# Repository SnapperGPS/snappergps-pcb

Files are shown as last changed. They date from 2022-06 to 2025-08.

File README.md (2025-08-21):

> *Are you looking for the open-source SnapperGPS hardware design files? You can find the files for the original version V1.0.0 in this repository and the files for an updated version V2.0.0 [in another repository](https://github.com/SnapperGPS/snappergps-pcb-2). For differences between both versions, please refer to the documentation over there. Jonas, May 2023*

# snappergps-pcb

The SnapperGPS receiver is a small, low-cost, and low-power GNSS receiver for non-real-time wildlife tracking. It employs the snapshot GNSS technology, which offloads the computationally expensive data processing to the cloud, and:

* Measures 32.0 mm x 27.3 mm,

* Operates for more than a year on a tiny 40 mAh battery,

* Has enough memory to provide almost 11,000 position fixes,

* Captures fixes in user-defined time intervals or externally triggered,

* Needs only 12 ms of signal reception for a fix,

* Employs multiple satellite systems for high reliability (GPS, Galileo, and BeiDou),

* Achieves a median real-world tracking accuracy of about 12 m (before smoothing),

* Maintains a real-time clock to accurately timestamp the fixes,

* Measures the temperature in addition, and

* Is configured via USB in your browser without the need to install a driver or an app.

This repository contains the hardware design files that can be used to replicate a SnapperGPS receiver.

If you use SnapperGPS hardware or software for research, please consider citing our publications.

For the hardware:

> Jonas Beuchert, Amanda Matthes, and Alex Rogers. 2023. SnapperGPS: Open Hardware for Energy-Efficient, Low-Cost Wildlife Location Tracking with Snapshot GNSS. Journal of Open Hardware, 7(1): 2, pp. 1–13. [https://doi.org/10.5334/joh.48](https://openhardware.metajnl.com/articles/10.5334/joh.48/).

For the cloud-processing software:

> Jonas Beuchert and Alex Rogers. 2021. SnapperGPS: Algorithms for Energy-Efficient Low-Cost Location Estimation Using GNSS Signal Snapshots. In SenSys ’21: ACM Conference on Embedded Networked Sensor Systems, November, 2021, Coimbra, Portugal. ACM, New York, NY, USA, 13 pages. https://doi.org/10.1145/3485730.3485931.

**Table of Contents**

1. [Workflow](#workflow)

2. [Getting started](#getting-started)

3. [Repository Structure](#repository-structure)

4. [Professional Manufacturing](#professional-manufacturing)

5. [Hand Assembly](#hand-assembly)

6. [Testing](#testing)

7. [Hardware Overview](#hardware-overview)

8. [Pinout](#pinout)

9. [Bill of Materials](#bill-of-materials)

10. [Additional Resources](#additional-resources)

11. [Acknowledgements](#acknowledgements)

## Workflow

- Get/build your SnapperGPS receiver (see sections below).
- [Configure](https://snappergps.info/configure) your SnapperGPS receiver in your browser for your deployment.
- Deploy your SnapperGPS receiver.
- The SnapperGPS receiver captures GNSS snapshots according to your configuration.
- Recover your SnapperGPS receiver.
- [Upload](https://snappergps.info/upload) the data from your SnapperGPS receiver to our server.
- [Download](https://snappergps.info/view) the track of your surveilled animal.

## Getting started

You already have a SnapperGPS receiver? See [here](GETTING-STARTED.md) how to get started.

You need to build one first? Keep reading.

## Repository Structure

The two files `.brd` and `.sch` are CAD files that contain the PCB's board design and schematic, respectively. They have been created with Autodesk EAGLE 9.6.2, but should be compatible with other electronic design software.

The table `.csv` contains the bill of materials (BOM).

The directory `CAMOutputs` includes the Gerber files and drill file, which are necessary for PCB manufacturing.

The two files `.mnb` and `.mnt` can be used for a pick-and-place machine and describe the component positions and orientations on the bottom and top layer, respectively.

## Professional Manufacturing

The simplest way to replicate SnapperGPS is to upload the BOM, the Gerber files, the drill file, and the pick and place files to an online PCB manufacturing and assembly service. They will source the components, print the PCB, and assemble the board.

We recommend a thickness between 0.8 and 1.6 mm for the two-layered board. The substrate can be FR-4 and hot air solder levelling (HASL) or electroless nickel immersion gold (ENIG) can be used for the finish.

You can find an FAQ on professional manufacturing in [the discussions forum](https://github.com/orgs/SnapperGPS/discussions/22).

## Hand Assembly

An alternative to prefessional manufacturing is to just obtain the SnapperGPS PCB from a PCB manufacturer and to manually assembly the board.
Hand-soldering a board takes less than 2 h for a skilled person, but requires intermediate equipment and skills and potentially additional time for testing, debugging, and re-work.

A laser-cut stencil for applying the solder paste can be helpful and can often be ordered together with the PCB.
In addition, the following materials and equipment are required:

* Soldering paste

* Syringe

* Spatula

* Tweezers

* Hot plate, re-flow oven, or hot air gun

* Flux pen (optional, for re-work)

* Multi-meter (optional, for debugging)

Proceed with the following steps to assemble a SnapperGPS PCB:

* Rigidly fix the PCB to a surface with the top layer pointing up.

* Fix the stencil on the PCB.

* Use the syringe to apply solder paste to the stencil.

* Use the spatula to distribute the solder paste such that all pads on the PCB are covered.

* Remove the stencil.

* Check that all pads are covered with solder paste.

* If not, manually apply solder paste.

* Use tweezers to place the components on the PCB.

* Heat the PCB following the re-flow profile of the used solder paste.

* Test the PCB (see below).

* If it does not work, identify problematic PCB sections and re-work, e.g., by applying flux and re-flowing the board. The most common issues are shorts and missing solder paste on some pads, which can be identified by using a multi-meter for continuity testing, but it is also possible that a component is placed incorrectly.

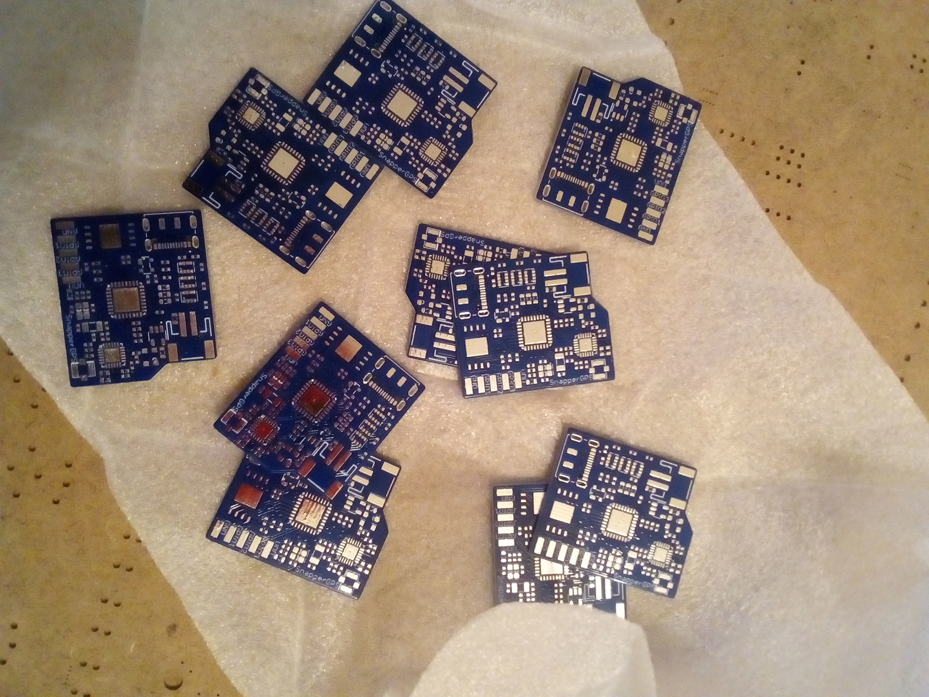
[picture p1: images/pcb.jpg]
SnapperGPS PCB
|  | 
|:--:| 
| *Figure 1: Several SnapperGPS PCBs ready for hand assembly.* |

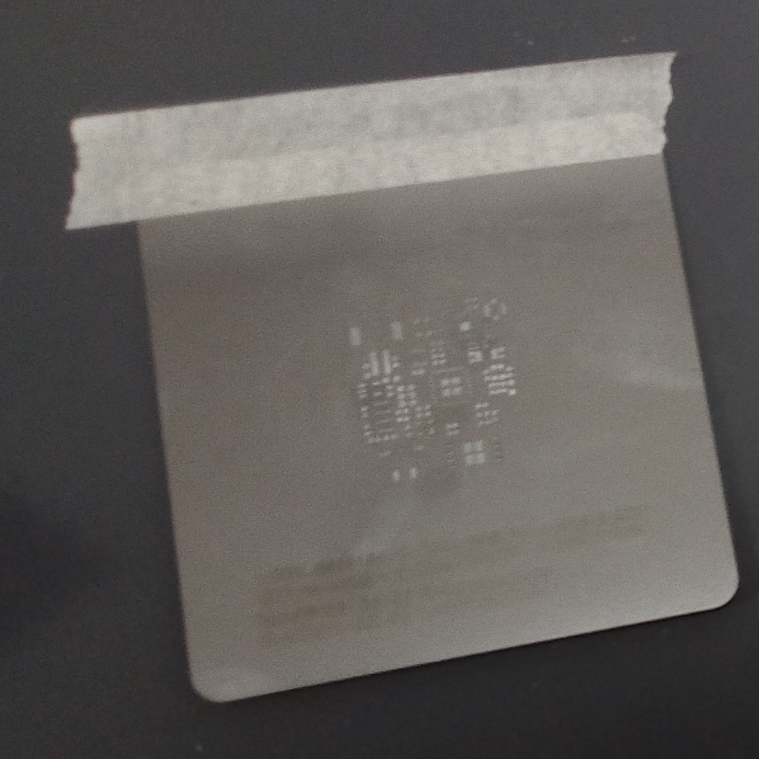
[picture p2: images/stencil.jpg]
Stencil
|  | 
|:--:| 
| *Figure 2: A stencil on top of a SnapperGPS PCB with solder paste applied to it.* |

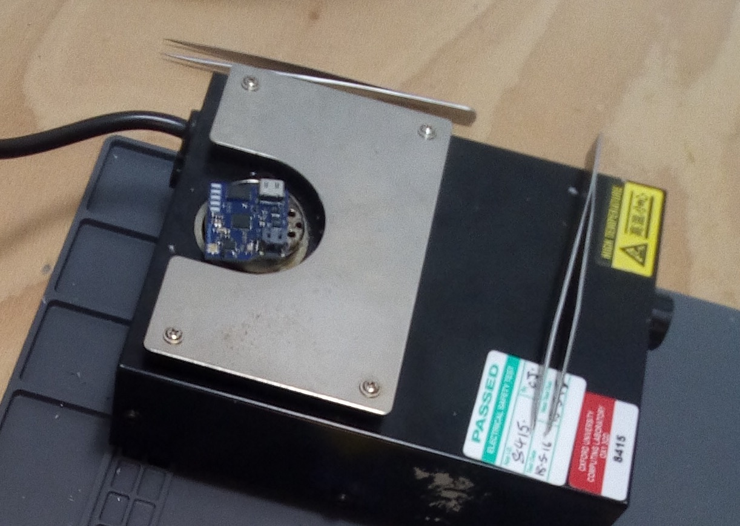
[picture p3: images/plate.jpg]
Hot plate
|  | 
|:--:| 
| *Figure 3: A SnapperGPS PCB with solder paste and components on a hot plate while re-flowing.* |

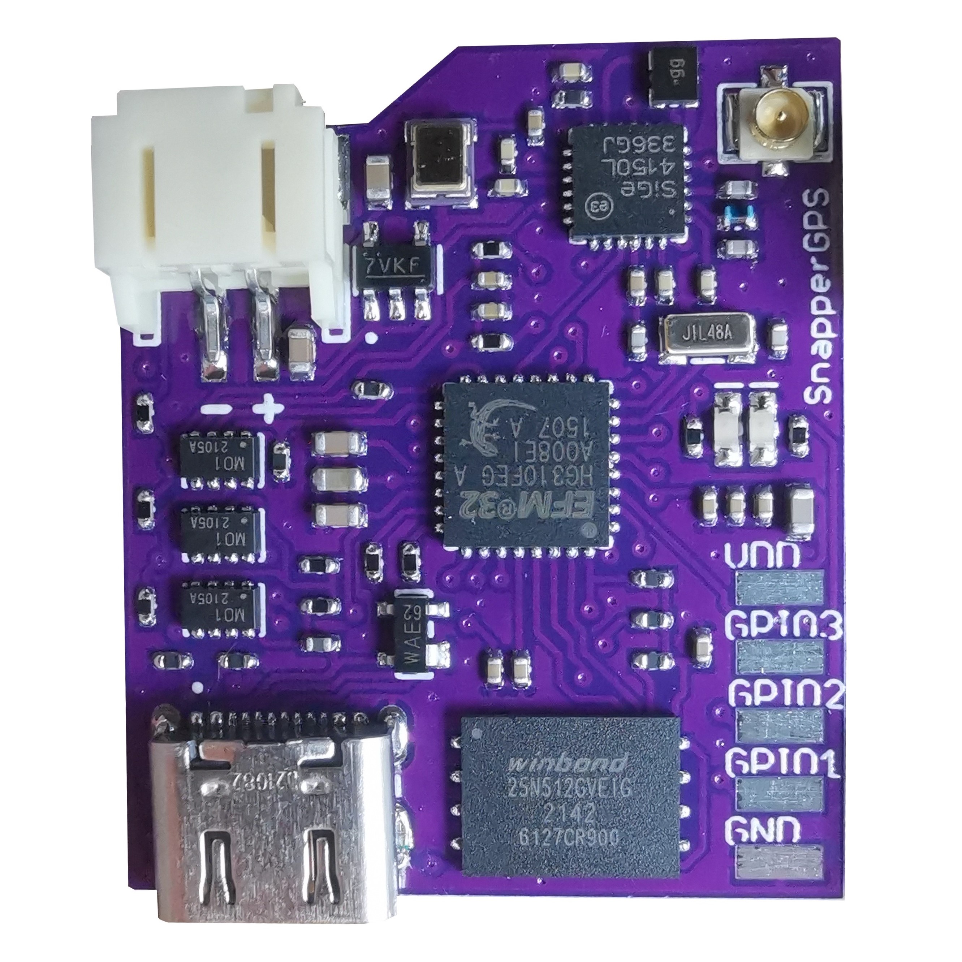
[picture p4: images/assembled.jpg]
Assembled SnapperGPS PCB
|  | 
|:--:| 
| *Figure 4: An assembled SnapperGPS receiver.* |

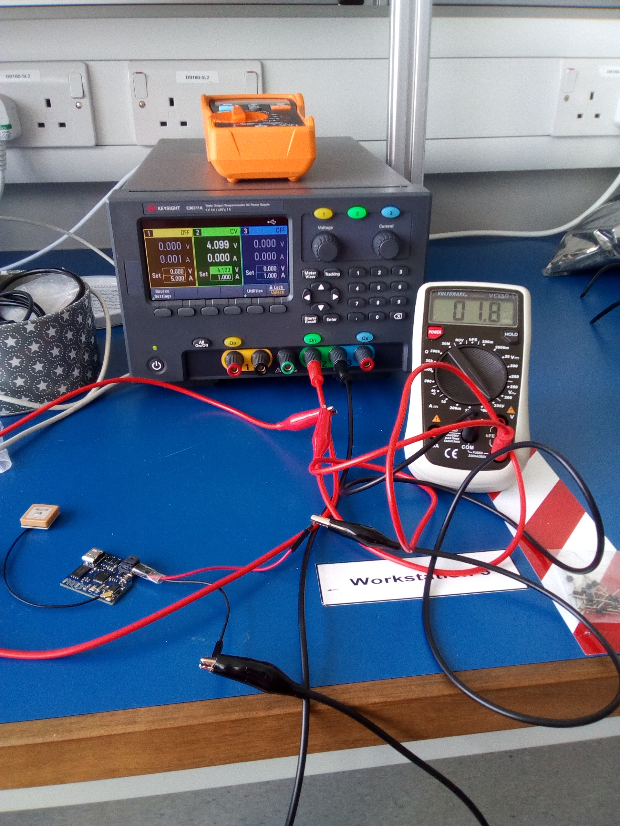
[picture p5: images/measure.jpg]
Measuring the current
|  | 
|:--:| 
| *Figure 5: Measuring the current consumption of an assembled SnapperGPS receiver (bottom left) with a multi-meter (right), a DC voltage source (centre), two jumper wires, and alligator clips.* |

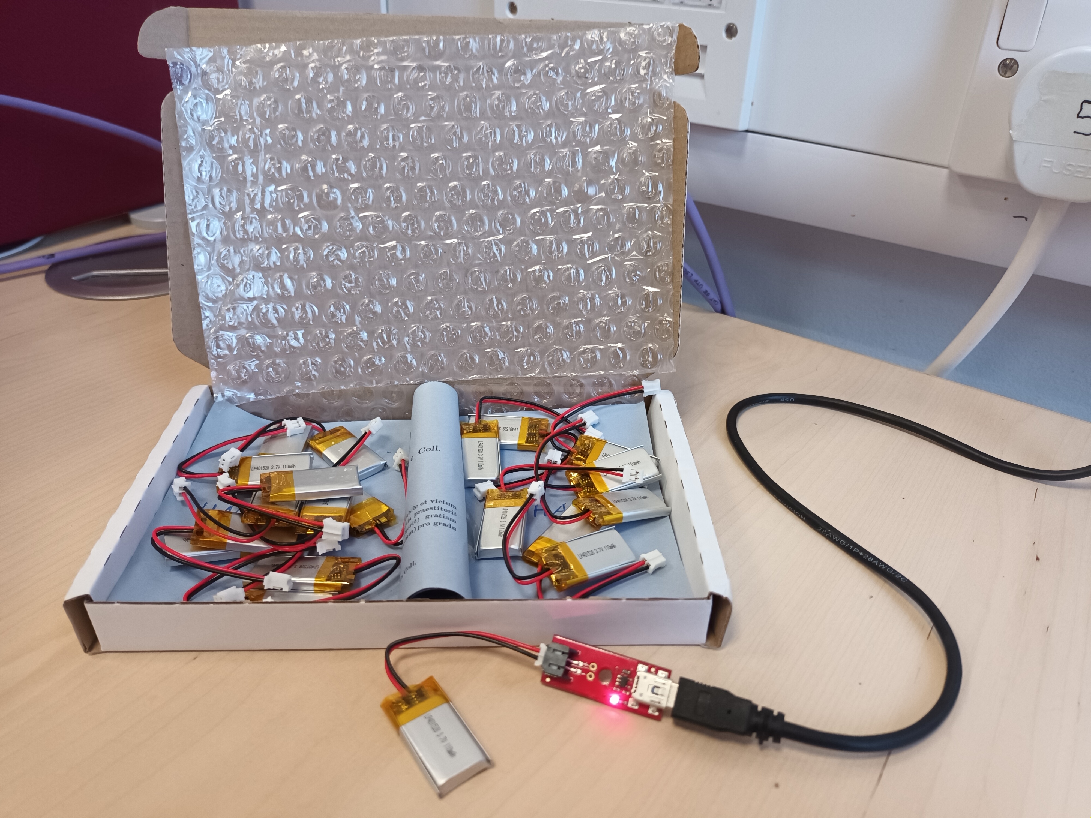
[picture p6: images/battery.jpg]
Charging a battery
|  | 
|:--:| 
| *Figure 6: Charging a 110 mAh lithium-ion polymer battery via USB with a *SparkFun LiPo Charger Basic*.* |

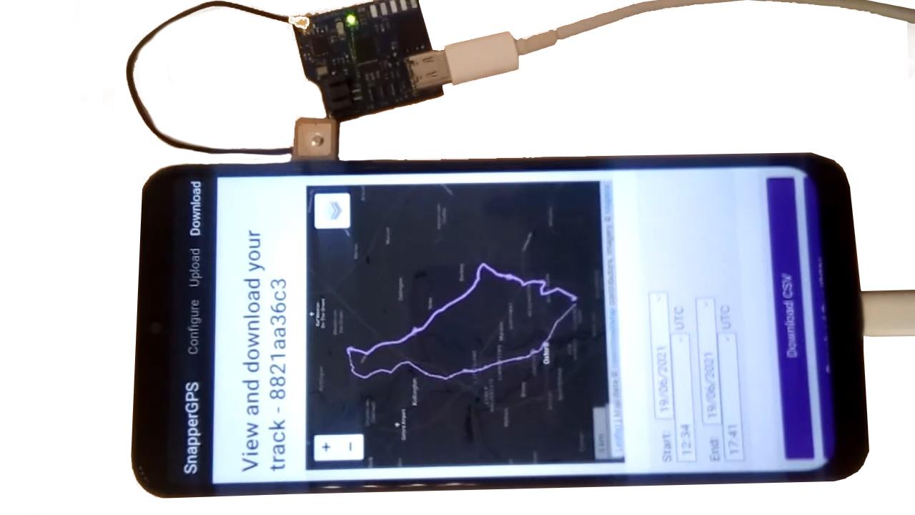
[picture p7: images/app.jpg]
SnapperGPS app
|  | 
|:--:| 
| *Figure 7: Testing a SnapperGPS receiver with the SnapperGPS app on an Android smartphone using a USB-C cable.* |

## Testing

If you replicated a SnapperGPS receiver yourself, you need to flash the SnapperGPS firmware first:

* Short the VDD pin and the SWCLK pin of the SnapperGPS receiver, e.g., with a paper clip.

* Connect the SnapperGPS receiver via a USB-C cable to a host computer.

* Download [the SnapperGPS firmware binary](https://github.com/SnapperGPS/snappergps-firmware/releases).

* Install [the AudioMoth Flash App](https://github.com/OpenAcousticDevices/AudioMoth-Flash-App/releases) **or** [the Silicon Labs Simplicity Commander](https://community.silabs.com/s/article/simplicity-commander).

* Use one of the two tools two flash the firmware binary to the SnapperGPS receiver. (If you use the AudioMoth Flash App, either use v1.4.0 or, if you use v1.6.0, then disable "Clear User Data When Flashing".)

* Remove the paper clip.

Now, you can continue with some basic testing:

* Open [the SnapperGPS web app](https://snappergps.info) in Microsoft Edge or Google Chrome or download it from [the Microsoft Store](https://apps.microsoft.com/store/detail/snappergps/9P9RPRS6LSMM) or [Google Play](https://play.google.com/store/apps/details?id=com.herokuapp.snapper_gps.twa). (Alternatively, you can also host the SnapperGPS web app yourself, as described in [the _snappergps-app_ repository](https://github.com/SnapperGPS/snappergps-app)).

* Go to the *Configure* page and click/tap on *Pair receiver*.

* The connected SnapperGPS receiver should now be selectable in a pop-up window.

* After pairing, confirm that the receiver information in the table on the top of the page is appropriate, including on-board time and firmware version. The snapshot count should be zero.

* Connect a LiPo battery to the SnapperGPS receiver, paying attention to the polarity markers on top of the PCB. Connect the black cable to the pin next to the *-* and the red cable to the pin next to the *+*.

* Check the measured battery voltage in the table at the top of the *Configure* page. We recommend charging the battery to at least 4.1 V before a long-term deployment.

* Connnect an active GNSS antenna of your choice via the U.FL connector to the SnapperGPS receiver.

* Select some configuration parameters in the app and click/tap on *Configure*.

* Disconnect the SnapperGPS receiver.

* Record a few snapshots outdoors.

* Reconnect the SnapperGPS receiver.

* Go to the *Upload* page and follow the instructions to upload the snapshots from the SnapperGPS receiver to the server. Please select only snapshots for processing that you collected outdoors.

* Once processing is complete, inspect the calculated track on the *Download* page. There are also links to some of our tracks for comparison.

Testing the localisation accuracy:

* Record some data outdoors at a location with known coordinates.

* Upload it via the SnapperGPS app.

* Calculate the horizontal error between the estimated locations and the ground truth.

* We obtained median errors of 10-12 m, depending on the scenario.

Measuring the power consumption:

* Configure a SnapperGPS receiver using the SnapperGPS app.

* Power the SnapperGPS receiver from an external DC source with 3.7-4.2 V.

* Place an ammeter in series with the source.

* The current should be 1-2 μA if the board is sleeping and the maximum current should be around 25 mA when capturing a snapshot. The charge consumption for a single snapshot should be <0.3 μAh.

Testing the flash memory:

* Record the maximum of 10901 snapshots.

* Transfer them to a host computer using the *Transfer data* button on the *Upload* page of the SnapperGPS web app.

* Ensure that all 10901 snapshots have been transferred and are provided as download.

## Hardware Overview

Please have a look at our [paper](https://doi.org/10.5334/joh.48).

## Pinout

We expose the three general-purpose input/output pins (GPIOs) PA0, PA1, and PA2 of the MCU as well as the supply voltage pin VDD and the ground pin GND at an edge of the PCB.
This allows to connect external modules to extend the functionality of the device.
This can be done by soldering wires on the rectangular pads.
For the functionality of the three pins, please refer to [the pinout section in the datasheet of the EFM32HG310](https://www.silabs.com/documents/public/data-sheets/efm32hg-datasheet.pdf#page=118).

We also expose the VDD, GND, RESET, SWCLK, and SWDIO pins of the MCU on the back of the PCB.
The last two ones allow for debugging or flashing using [Serial Wire Debug (SWD)](https://community.silabs.com/s/article/serial-wire-debug-swd-x).
All five circular pads have a spacing of 0.1 in and, hence, the same as common PCB headers.

All ten pads are labelled on the silkscreen of the PCB.

```
Front           │           │ Back
                │           │
                │           │ ○ GND
          VDD □ │           │
                │           │ ○ RESET
    GPIO3/PA2 □ │           │
                │           │ ○ SWCLK
    GPIO2/PA1 □ │           │
                │           │ ○ SWDIO
    GPIO1/PA0 □ │           │
                │           │ ○ VDD
          GND □ │           │
────────────────┘           │
```

## Bill of Materials

|Designator                                    |Qty|Manufacturer                  |Part #                                 |Description/Value                                            |Package/Footprint|Mounting Type|Notes                                                                          |Supplier URL                                                                                           |
|----------------------------------------------|--:|------------------------------|---------------------------------------|-------------------------------------------------------------|-----------------|-------------|-------------------------------------------------------------------------------|-------------------------------------------------------------------------------------------------------|
|C4, C8, C10, C12, C13, C14, C16, C17, C20, C23| 10|Murata                        |GRM155R60J104KA01D                     |Ceramic capacitor, 100 nF                                    |0402             |SMD          |                                                                               |https://www.digikey.com/en/products/detail/murata-electronics/GRM155R60J104KA01D/490-6287-1-ND/3845484 |
|C3, C5, C6, C7, C9                            |  5|Murata                        |GRM155R60J103KA01D                     |Ceramic capacitor, 10 nF                                     |0402             |SMD          |                                                                               |https://www.digikey.com/en/products/detail/murata-electronics/GRM155R60J103KA01D/490-6286-1-ND/3845483 |
|C2                                            |  1|Murata                        |GRM1555C1H101JA01J                     |Ceramic capacitor, 100 pF                                    |0402             |SMD          |                                                                               |https://www.digikey.com/en/products/detail/murata-electronics/GRM1555C1H101JA01J/490-7754-1-ND/4358006 |
|C1                                            |  1|Murata                        |GRM1555C1H220JA01D                     |Ceramic capacitor, 22 pF                                     |0402             |SMD          |                                                                               |https://www.digikey.com/en/products/detail/murata-electronics/GRM1555C1H220JA01D/490-5868-1-ND/3175200 |
|C21, C22                                      |  2|Murata                        |GRM1555C1H180JA01D                     |Ceramic capacitor, 18 pF                                     |0402             |SMD          |                                                                               |https://www.digikey.com/en/products/detail/murata-electronics/GRM1555C1H180JA01D/2854383               |
|C11, C19, C24, C25                            |  4|Murata                        |GRM188R60J105KA01D                     |Multi-layer ceramic capacitor, 1 uF, 6.3 V, X5R              |0603             |SMD          |                                                                               |https://www.digikey.com/en/products/detail/murata-electronics/GRM188R60J105KA01D/490-1550-1-ND/587755  |
|C18                                           |  1|Murata                        |GRM185R60J475ME15D                     |Multi-layer ceramic capacitor, 4.7 uF, 6.3 V, X5R            |0603             |SMD          |                                                                               |https://www.digikey.com/en/products/detail/murata-electronics/GRM185R60J475ME15D/490-3892-1-ND/965934  |
|C15                                           |  1|Murata                        |GRM188R60J106KE47D                     |Multi-layer ceramic capacitor, 10 uF, 6.3 V, X5R             |0603             |SMD          |                                                                               |https://www.digikey.com/en/products/detail/murata-electronics/GRM188R60J106KE47D/490-12538-1-ND/5797528|
|L1                                            |  1|Delta Electronics             |0402HS-390EKTS                        |Fixed inductor, 39 nH, 200 mA, 550 MOhm                      |0402             |SMD          |                                                                               |https://www.digikey.com/en/products/detail/0402HS-390EKTS/2035-0402HS-390EKTSCT-ND/10231211            |
|L2                                            |  1|Murata                        |BLM15HB221SH1D                         |Ferrite bead                                                 |0402             |SMD          |                                                                               |https://www.digikey.com/en/products/detail/murata-electronics/BLM15HB221SH1D/6798444                   |
|R11, R12                                      |  2|Yageo                         |RC0402FR-0715RL                        |Resistor, 15R                                                |0402             |SMD          |                                                                               |https://www.digikey.com/en/products/detail/yageo/RC0402FR-0715RL/311-15LRCT-ND/2827914                 |
|R15, R16                                      |  2|Yageo                         |RC0402FR-071KL                         |Resistor, 1K                                                 |0402             |SMD          |                                                                               |https://www.digikey.com/en/products/detail/yageo/RC0402FR-071KL/726513                                 |
|R10, R13, R17                                 |  3|Yageo                         |RC0402FR-074K7L                        |Resistor, 4K7                                                |0402             |SMD          |                                                                               |https://www.digikey.com/en/products/detail/yageo/RC0402FR-074K7L/311-4-7KLRCT-ND/2827881               |
|R7, R8                                        |  2|Yageo                         |RC0402FR-075K1L                        |Resistor, 5K1                                                |0402             |SMD          |                                                                               |https://www.digikey.com/en/products/detail/yageo/RC0402FR-075K1L/726624                                |
|R18                                           |  1|Yageo                         |RC0402FR-076K8L                        |Resistor, 6K8                                                |0402             |SMD          |                                                                               |https://www.digikey.com/en/products/detail/yageo/RC0402FR-076K8L/311-6-80KLRCT-ND/729589               |
|R14, R19                                      |  2|Yageo                         |RC0402FR-0710KL                        |Resistor, 10K                                                |0402             |SMD          |                                                                               |https://www.digikey.com/en/products/detail/yageo/RC0402FR-0710KL/726523                                |
|R1, R2, R3, R4, R5, R6, R9                    |  7|Yageo                         |RC0402FR-07100KL                       |Resistor, 100K                                               |0402             |SMD          |                                                                               |https://www.digikey.com/en/products/detail/yageo/RC0402FR-07100KL/311-100KLRCT-ND/729473               |
|Q2                                            |  1|Jauch Quartz                  |Q 0,032768-JTX310-12,5-10-T1-HMR-50K-LF|Crystal, 32.768 kHz ±10 ppm, 12.5 pF, 50 kOhm                |2-SMD            |SMD          |Possible substitutes: Epsom, X1A0001410004 FC-135R 32.768KHZ 9PF or Jauch Quartz, Q 0,032768-JTX310-12,5-10-T1-HMR-60K-LF|https://www.digikey.com/en/products/detail/jauch-quartz/Q-0-032768-JTX310-12-5-10-T1-HMR-50K-LF/8108077|
|D1                                            |  1|Rohm Semiconductor            |SML-D12M1WT86                          |LED, yellow-green, 572 nm, 2.2 V                             |0603             |SMD          |                                                                               |https://www.digikey.com/en/products/detail/rohm-semiconductor/SML-D12M1WT86/SML-D12M1WT86CT-ND/5843861 |
|D2                                            |  1|Rohm Semiconductor            |SML-D12U1WT86                          |LED, red, 620 nm, 2.2 V                                      |0603             |SMD          |                                                                               |https://www.digikey.com/en/products/detail/rohm-semiconductor/SML-D12U1WT86/SML-D12U1WT86CT-ND/5843858 |
|TCXO1                                         |  1|Connor Winfield               |D32G-016.368M                          |Temperature compensated oscillator, 16.384 MHz               |3.2x2.5          |SMD          |Possible substitutes: EPSON, X1G005441030112 or TXC Corporation, 7Q-16.368MBG-T|https://www.digikey.com/en/products/detail/connor-winfield/D32G-016-368M/3641696                       |
|U2                                            |  1|Skyworks Solutions Inc.       |SE4150L-R                              |RF receiver                                                  |24-QFN           |SMD          |                                                                               |https://www.digikey.com/en/products/detail/skyworks-solutions-inc/SE4150L-R/863-1354-1-ND/2745473      |
|SAW1                                          |  1|Abracon LLC                   |AFS20A42-1575.42-T3                    |SAW filter, 1.575 GHz, BW 42 MHz                             |4-SMD            |SMD          |Possible substitute: AFS20A02-1575.42-T3                                       |https://www.digikey.com/en/products/detail/abracon-llc/AFS20A42-1575-42-T3/535-12069-1-ND/4075659      |
|U1                                            |  1|Silicon Labs                  |EFM32HG310F64G-C-QFN32R                |Microcontroller                                              |32-QFN           |SMD          |Possible substitutes: EFM32HG310F64G-A-QFN32R or EFM32HG310F64G-B-QFN32R       |https://www.digikey.com/en/products/detail/silicon-labs/EFM32HG310F64G-C-QFN32R/336-6165-1-ND/10314104 |
|U3                                            |  1|Nexperia                      |PRTR5V0U2AX,235                        |TVS diode, 5.5 V                                             |SOT143B          |SMD          |                                                                               |https://www.digikey.com/en/products/detail/nexperia-usa-inc/PRTR5V0U2AX235/1727-5862-1-ND/2698064      |
|IC1                                           |  1|Winbond Electronics           |W25N512GVEIG                           |NAND flash, 512 Mbit                                         |WSON-8           |SMD          |                                                                               |https://www.digikey.com/en/products/detail/W25N512GVEIG/256-W25N512GVEIG-ND/12143334                   |
|J3                                            |  1|TE Connectivity AMP Connectors|1909763-1                              |U.FL connector jack, 50 Ohm                                  |                 |SMD          |                                                                               |https://www.digikey.com/en/products/detail/1909763-1/A118077CT-ND/4729711                              |
|Q1, Q3, Q4                                    |  3|Rohm Semiconductor            |TT8M1TR                                |Mosfet array N and P-channel, 20 V, 2.5 A, 1 W               |8-SMD            |SMD          |                                                                               |https://www.digikey.com/en/products/detail/rohm-semiconductor/TT8M1TR/5042837                          |
|U4                                            |  1|ABLIC U.S.A. Inc.             |S-1318D33-M5T1U4                       |Linear voltage regulator IC, positive fixed, 1 output, 100 mA|SOT-23-5         |SMD          |                                                                               |https://www.digikey.com/en/products/detail/ablic-inc/S-1318D33-M5T1U4/10313979                         |
|J1                                            |  1|JAE Electronics               |DX07S016JA1R1500                       |USB-C receptacle connector, 24 Pins (16+8 dummy), right angle|                 |through-hole |                                                                               |https://www.digikey.com/en/products/detail/jae-electronics/DX07S016JA1R1500/11585731                   |
|J2                                            |  1|JST Sales America Inc.        |S2B-PH-SM4-TB                          |Connector header, right angle, 2 position, 2.00 mm           |                 |SMD          |                                                                               |https://www.digikey.com/en/products/detail/jst-sales-america-inc/S2B-PH-SM4-TB-LF-SN/926655            |
|                                              |   |                              |                                       |                                                             |                 |             |                                                                               |                                                                                                       |

The BOM differs slightly from the one for initial SnapperGPS test boards, which was only $14 in a batch of 100.
For example, we used cheaper TCXOs, the X1G005441030112 manufactured by EPSON or the 7Q-16.368MBG-T from the TXC Corporation, which cost around $2 instead of the expensive D32G-016.368M that costs $7-$8.
We had to introduce this change because of the on-going global supply chain disruptions and recommend to revert to one of the initial choices for replications, if possible, to reduce the overall cost.

## Additional resources

## Acknowledgements

SnapperGPS is developed by
[Jonas Beuchert](https://users.ox.ac.uk/~kell5462/),
[Amanda Matthes](https://amanda-matthes.github.io/), and
[Alex Rogers](https://www.cs.ox.ac.uk/people/alex.rogers/)
in the Department of Computer Science
of the University of Oxford.

Jonas Beuchert and Amanda Matthes are
funded by the EPSRC Centre for Doctoral Training in
Autonomous Intelligent Machines and Systems
(DFT00350-DF03.01, DFT00350-DF03.05) and develop
SnapperGPS as part of their doctoral studies.
The implementation of SnapperGPS 
was co-funded by an EPSRC IAA Technology Fund
(D4D00010-BL14).

[Amanda Matthes](https://github.com/amanda-matthes) owns the copyright of the current SnapperGPS logo/icon that is on the bottom layer silkscreen of the PCB.

##

This documentation is licensed under a
[Creative Commons Attribution 4.0 International License][cc-by].

[][cc-by]

[cc-by]: http://creativecommons.org/licenses/by/4.0/
[cc-by-image]: https://i.creativecommons.org/l/by/4.0/88x31.png

SnapperGPS V1.0.0 is certified as open source hardware by the Open Source Hardware Association with UID [UK000044](https://certification.oshwa.org/uk000044.html).

OSHWA certification

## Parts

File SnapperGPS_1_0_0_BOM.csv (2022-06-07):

Designator | Qty | Manufacturer | Part # | Description/Value | Package/Footprint | Mounting Type | Notes | Supplier URL | Price (1 set) [USD] | Price (100 sets) [USD] | Price (1000 sets) [USD]
C4, C8, C10, C12, C13, C14, C16, C17, C20, C23 | 10 | Murata | GRM155R60J104KA01D | Ceramic capacitor, 100 nF | 402 | SMD |  | https://www.digikey.com/en/products/detail/murata-electronics/GRM155R60J104KA01D/490-6287-1-ND/3845484 | 0.33 | 14.6 | 81.7
C3, C5, C6, C7, C9 | 5 | Murata | GRM155R60J103KA01D | Ceramic capacitor, 10 nF | 402 | SMD |  | https://www.digikey.com/en/products/detail/murata-electronics/GRM155R60J103KA01D/490-6286-1-ND/3845483 | 0.5 | 4.43 | 29.1
C2 | 1 | Murata | GRM1555C1H101JA01J | Ceramic capacitor, 100 pF | 402 | SMD |  | https://www.digikey.com/en/products/detail/murata-electronics/GRM1555C1H101JA01J/490-7754-1-ND/4358006 | 0.1 | 0.81 | 4.54
C1 | 1 | Murata | GRM1555C1H220JA01D | Ceramic capacitor, 22 pF | 402 | SMD |  | https://www.digikey.com/en/products/detail/murata-electronics/GRM1555C1H220JA01D/490-5868-1-ND/3175200 | 0.1 | 0.81 | 4.57
C21, C22 | 2 | Murata | GRM1555C1H180JA01D | Ceramic capacitor, 18 pF | 402 | SMD |  | https://www.digikey.com/en/products/detail/murata-electronics/GRM1555C1H180JA01D/2854383 | 0.2 | 2.32 | 13
C11, C19, C24, C25 | 4 | Murata | GRM188R60J105KA01D | Multi-layer ceramic capacitor, 1 uF, 6.3 V, X5R | 603 | SMD |  | https://www.digikey.com/en/products/detail/murata-electronics/GRM188R60J105KA01D/490-1550-1-ND/587755 | 0.4 | 11 | 61.84
C18 | 1 | Murata | GRM185R60J475ME15D | Multi-layer ceramic capacitor, 4.7 uF, 6.3 V, X5R | 603 | SMD |  | https://www.digikey.com/en/products/detail/murata-electronics/GRM185R60J475ME15D/490-3892-1-ND/965934 | 0.3 | 11.67 | 72.02
C15 | 1 | Murata | GRM188R60J106KE47D | Multi-layer ceramic capacitor, 10 uF, 6.3 V, X5R | 603 | SMD |  | https://www.digikey.com/en/products/detail/murata-electronics/GRM188R60J106KE47D/490-12538-1-ND/5797528 | 0.15 | 5.07 | 29.44
L1 | 1 | Delta Electronics | 0402HS-390EKTS | Fixed inductor, 39 nH, 200 mA, 550 MOhm | 402 | SMD |  | https://www.digikey.com/en/products/detail/0402HS-390EKTS/2035-0402HS-390EKTSCT-ND/10231211 | 0.26 | 15.68 | 109.72
L2 | 1 | Murata | BLM15HB221SH1D | Ferrite bead | 402 | SMD |  | https://www.digikey.com/en/products/detail/murata-electronics/BLM15HB221SH1D/6798444 | 0.1 | 4.36 | 25.08
R11, R12 | 2 | Yageo | RC0402FR-0715RL | Resistor, 15R | 402 | SMD |  | https://www.digikey.com/en/products/detail/yageo/RC0402FR-0715RL/311-15LRCT-ND/2827914 | 0.2 | 1.32 | 5.98
R15, R16 | 2 | Yageo | RC0402FR-071KL | Resistor, 1K | 402 | SMD |  | https://www.digikey.com/en/products/detail/yageo/RC0402FR-071KL/726513 | 0.2 | 1.32 | 5.98
R10, R13, R17 | 3 | Yageo | RC0402FR-074K7L | Resistor, 4K7 | 402 | SMD |  | https://www.digikey.com/en/products/detail/yageo/RC0402FR-074K7L/311-4-7KLRCT-ND/2827881 | 0.3 | 1.98 | 7.77
R7, R8 | 2 | Yageo | RC0402FR-075K1L | Resistor, 5K1 | 402 | SMD |  | https://www.digikey.com/en/products/detail/yageo/RC0402FR-075K1L/726624 | 0.2 | 1.32 | 5.98
R18 | 1 | Yageo | RC0402FR-076K8L | Resistor, 6K8 | 402 | SMD |  | https://www.digikey.com/en/products/detail/yageo/RC0402FR-076K8L/311-6-80KLRCT-ND/729589 | 0.1 | 0.66 | 2.99
R14, R19 | 2 | Yageo | RC0402FR-0710KL | Resistor, 10K | 402 | SMD |  | https://www.digikey.com/en/products/detail/yageo/RC0402FR-0710KL/726523 | 0.2 | 1.32 | 5.98
R1, R2, R3, R4, R5, R6, R9 | 7 | Yageo | RC0402FR-07100KL | Resistor, 100K | 402 | SMD |  | https://www.digikey.com/en/products/detail/yageo/RC0402FR-07100KL/311-100KLRCT-ND/729473 | 0.7 | 4.62 | 14.98
Q2 | 1 | Jauch Quartz | Q 0,032768-JTX310-12,5-10-T1-HMR-50K-LF | Ctystal, 32.768 kHz ±10 ppm, 12.5 pF, 50 kOhm | 2-SMD | SMD | Possible substitute: Epsom, X1A0001410004 FC-135R 32.768KHZ 9PF | https://www.digikey.com/en/products/detail/jauch-quartz/Q-0-032768-JTX310-12-5-10-T1-HMR-50K-LF/8108077 | 0.86 | 62.7 | 495
D1 | 1 | Rohm Semiconductor | SML-D12M1WT86 | LED, yellow-green, 572 nm, 2.2 V | 603 | SMD |  | https://www.digikey.com/en/products/detail/rohm-semiconductor/SML-D12M1WT86/SML-D12M1WT86CT-ND/5843861 | 0.22 | 5.51 | 39.86
D2 | 1 | Rohm Semiconductor | SML-D12U1WT86 | LED, red, 620 nm, 2.2 V | 603 | SMD |  | https://www.digikey.com/en/products/detail/rohm-semiconductor/SML-D12U1WT86/SML-D12U1WT86CT-ND/5843858 | 0.22 | 5.51 | 39.86
TCXO1 | 1 | Connor Winfield | D32G-016.368M | Temperature compensated oscillator, 16.384 MHz | 3.2x2.5 | SMD | Possible substitutes: EPSON, X1G005441030112 or TXC Corporation, 7Q-16.368MBG-T | https://www.digikey.com/en/products/detail/connor-winfield/D32G-016-368M/3641696 | 8 | 700 | 7000
U2 | 1 | Skyworks Solutions Inc. | SE4150L-R | RF receiver | 24-QFN | SMD |  | https://www.digikey.com/en/products/detail/skyworks-solutions-inc/SE4150L-R/863-1354-1-ND/2745473 | 0.86 | 86.4 | 864
SAW1 | 1 | Abracon LLC | AFS20A42-1575.42-T3 | SAW filter, 1.575 GHz, BW 42 MHz | 4-SMD | SMD |  | https://www.digikey.com/en/products/detail/abracon-llc/AFS20A42-1575-42-T3/535-12069-1-ND/4075659 | 1.05 | 71.37 | 543.74
U1 | 1 | Silicon Labs | EFM32HG310F64G-C-QFN32R | Microcontroller | 32-QFN | SMD |  | https://www.digikey.com/en/products/detail/silicon-labs/EFM32HG310F64G-C-QFN32R/336-6165-1-ND/10314104 | 5.91 | 435.04 | 3703.46
U3 | 1 | Nexperia | PRTR5V0U2AX,235 | TVS diode, 5.5 V | SOT143B | SMD |  | https://www.digikey.com/en/products/detail/nexperia-usa-inc/PRTR5V0U2AX235/1727-5862-1-ND/2698064 | 0.66 | 42.47 | 257.87
IC1 | 1 | Winbond Electronics | W25N512GVEIG | NAND flash, 512 Mbit | WSON-8 | SMD |  | https://www.digikey.com/en/products/detail/W25N512GVEIG/256-W25N512GVEIG-ND/12143334 | 2.9 | 228.68 | 2051.92
J3 | 1 | TE Connectivity AMP Connectors | 1909763-1 | U.FL connector jack, 50 Ohm |  | SMD |  | https://www.digikey.com/en/products/detail/1909763-1/A118077CT-ND/4729711 | 0.51 | 36.55 | 595.9
Q1, Q3, Q4 | 3 | Rohm Semiconductor | TT8M1TR | Mosfet array N and P-channel, 20 V, 2.5 A, 1 W | 8-SMD | SMD |  | https://www.digikey.com/en/products/detail/rohm-semiconductor/TT8M1TR/5042837 | 1.56 | 86.58 | 487.08
U4 | 1 | ABLIC U.S.A. Inc. | S-1318D33-M5T1U4 | Linear voltage regulator IC, positive fixed, 1 output, 100 mA | SOT-23-5 | SMD |  | https://www.digikey.com/en/products/detail/ablic-inc/S-1318D33-M5T1U4/10313979 | 1.58 | 109.94 | 908.2
J1 | 1 | JAE Electronics | DX07S016JA1R1500 | USB-C receptacle connector, 24 Pins (16+8 dummy), right angle |  | through-hole |  | https://www.digikey.com/en/products/detail/jae-electronics/DX07S016JA1R1500/11585731 | 1.67 | 129.65 | 1080.44
J2 | 1 | JST Sales America Inc. | S2B-PH-SM4-TB | Connector header, right angle, 2 position, 2.00 mm |  | SMD |  | https://www.digikey.com/en/products/detail/jst-sales-america-inc/S2B-PH-SM4-TB-LF-SN/926655 | 0.54 | 39.08 | 339.84
 |  |  |  |  |  |  |  |  | 31.55 | 2124.54 | 18900.69

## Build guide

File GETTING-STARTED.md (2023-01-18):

# SnapperGPS: Getting started

You just obtained your first SnapperGPS receiver or built one yourself? Here is how to get started with a quick test. If you face any problems on the way, check our troubleshooting section on [https://snappergps.info/](https://snappergps.info/), ask a question [on GitHub](https://github.com/orgs/SnapperGPS/discussions), or create [a new troubleshooting issue](https://github.com/SnapperGPS/snappergps-pcb/issues).

## What is in the box?

SnapperGPS receivers come as assembled PCBs, but without any further protection or peripherals.

| A bare-bone SnapperGPS receiver |
|:--:|
| *Figure 1: A bare-bone SnapperGPS receiver.* |

## What you need in addition.

To make your SnapperGPS receiver fully functional, you need the following items:
-	An active GPS-L1 antenna with [a U.FL/IPEX connector](https://en.wikipedia.org/wiki/Hirose_U.FL), for example, [an Echo 27](https://www.siretta.com/products/antennas/echo-27/), [an Abracon APAM1368YB13V3.0](https://abracon.com/parametric/antennas/APAM1368YB13V3.0), or [an Abracon APAM2764YK0175](https://abracon.com/parametric/antennas/APAM2764YK0175). More information [here](https://github.com/SnapperGPS/snappergps-pcb/discussions/10).
-	A lithium-ion polymer (LiPo) battery with a JST-PH connector to power your SnapperGPS receiver during a deployment, for example [this one with 40 mAh](https://www.sparkfun.com/products/13852) or [this one with 110 mAh](https://www.sparkfun.com/products/13853). Make sure that the polarity is correct, i.e., the same as in Figure 2 and **not** as in Figure 3.
-	Optionally, a charger for your LiPo battery. More information [here](https://github.com/SnapperGPS/snappergps-pcb/discussions/6).
-	A USB-C cable to connect your SnapperGPS receiver to your laptop, desktop computer, phone, or tablet. This must be a power+data cable, not a power-only cable.

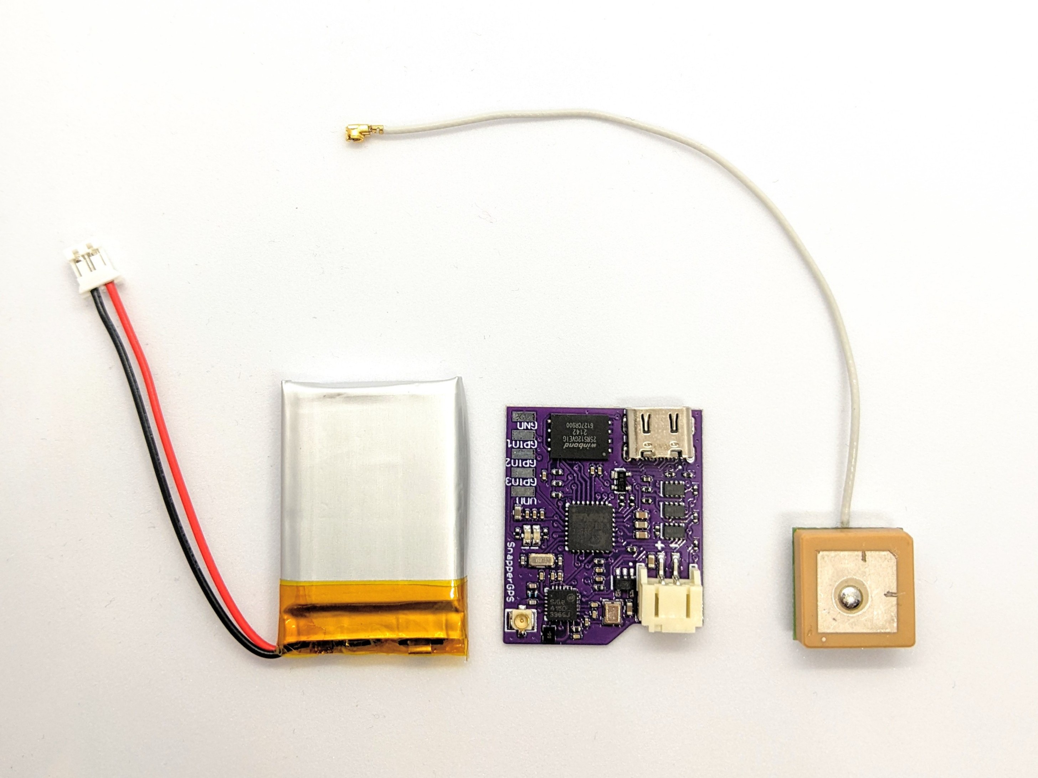
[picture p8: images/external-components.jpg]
A SnapperGPS receiver, an Echo 27 antenna (right), and a 400 mAh lithium-polymer battery (left)
|  |
|:--:|
| *Figure 2: A SnapperGPS receiver, an Echo 27 antenna (right), and a lithium-ion polymer battery with a JST-PH connector with the correct polarity (left).* |

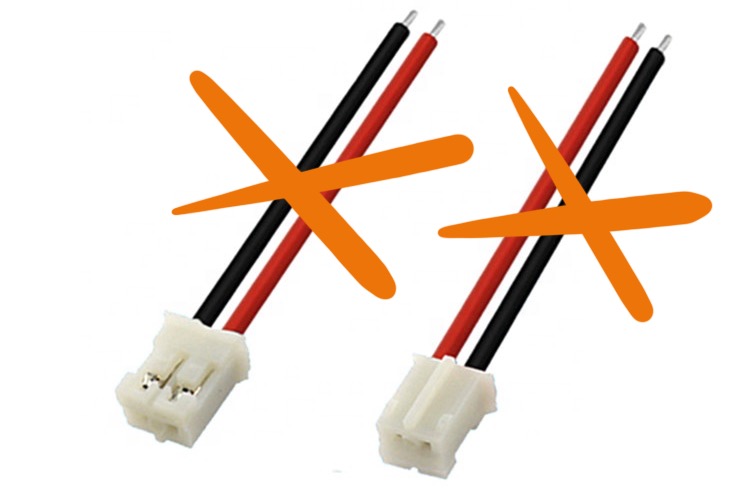
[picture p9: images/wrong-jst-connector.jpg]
JST-PH connectors with the incorrect polarity.)
|  |
|:--:|
| *Figure 3: JST-PH connectors with the incorrect polarity. The red and the black cable are swapped in contrast to the connector in Figure 1. Do not use a battery with this polarity with SnapperGPS.* |

## How to assemble your tag.

Connect your active GPS-L1 antenna to the circular U.FL connector. Make sure that the connection is tight.

Next, connect your battery to the plastic JST connector of your SnapperGPS receiver. Make sure that the black cable is connected to the part of the connector that is labelled with “-” and the red cable to the one labelled with “+”. If the polarity is inverted, you may damage your SnapperGPS receiver.

Finally, connect a USB-C cable to the USB-C port of your SnapperGPS receiver.

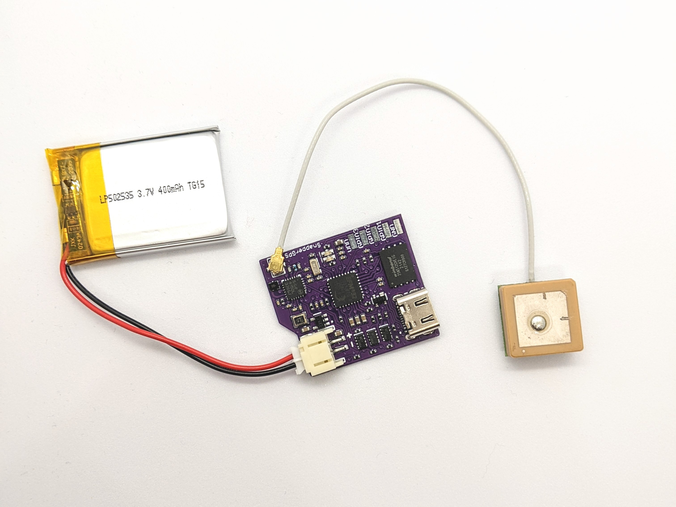
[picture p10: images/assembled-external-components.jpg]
A SnapperGPS receiver with peripherals
|  |
|:--:|
| *Figure 4: A SnapperGPS receiver with peripherals.* |

## Connect to your SnapperGPS receiver.

Connect your SnapperGPS receiver via USB to your laptop, desktop computer, tablet, or phone. (Note: iOS and iPadOS are not supported.)

Go to [https://snappergps.info/](https://snappergps.info/) in a browser like Microsoft Edge or Google Chrome. (Note: Mozilla Firefox and Apple Safari are not supported, for example.)

Click on “Configure” and then on “Pair Receiver”. If your SnapperGPS receiver is connected via USB, you should see it in a pop-up and should be able to select it.

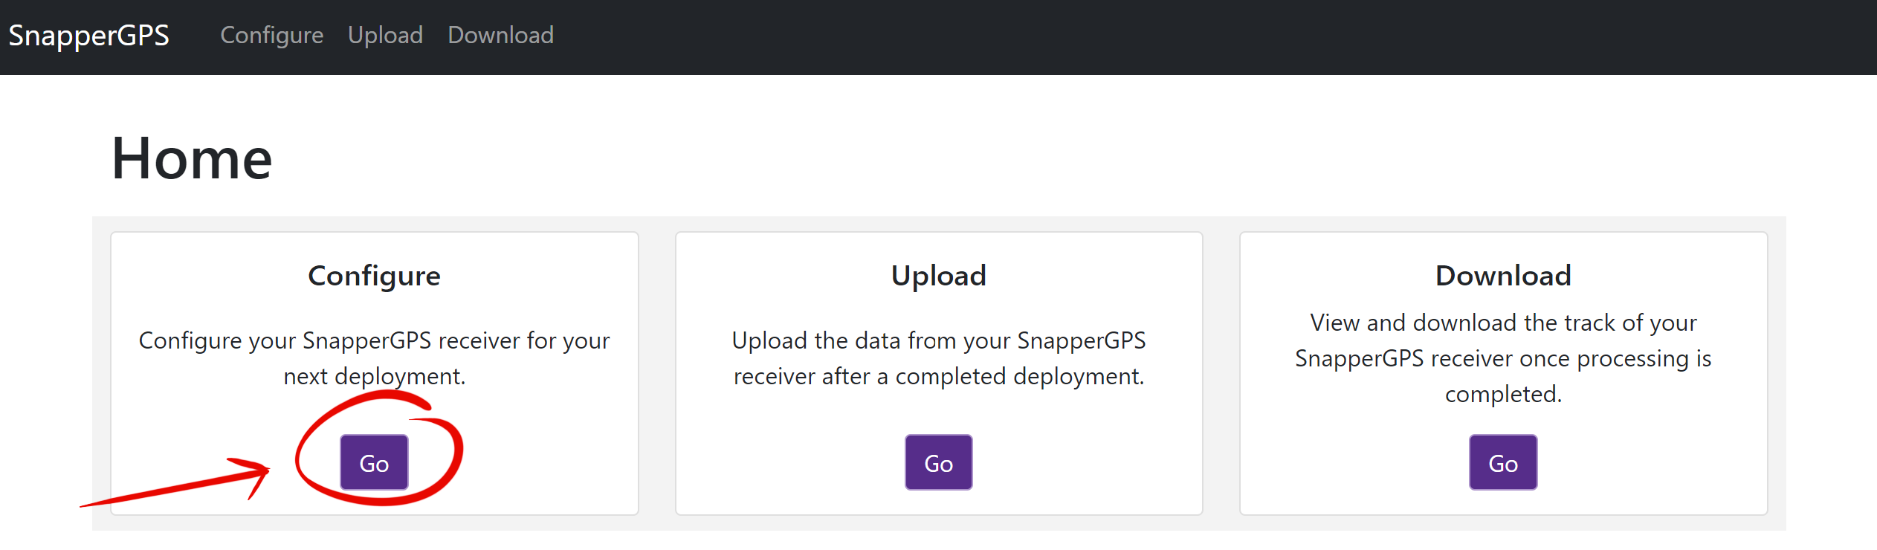
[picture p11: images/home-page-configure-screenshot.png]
Home page of https://snappergps.info/
|  |
|:--:|
| *Figure 5: Home page of https://snappergps.info/.* |

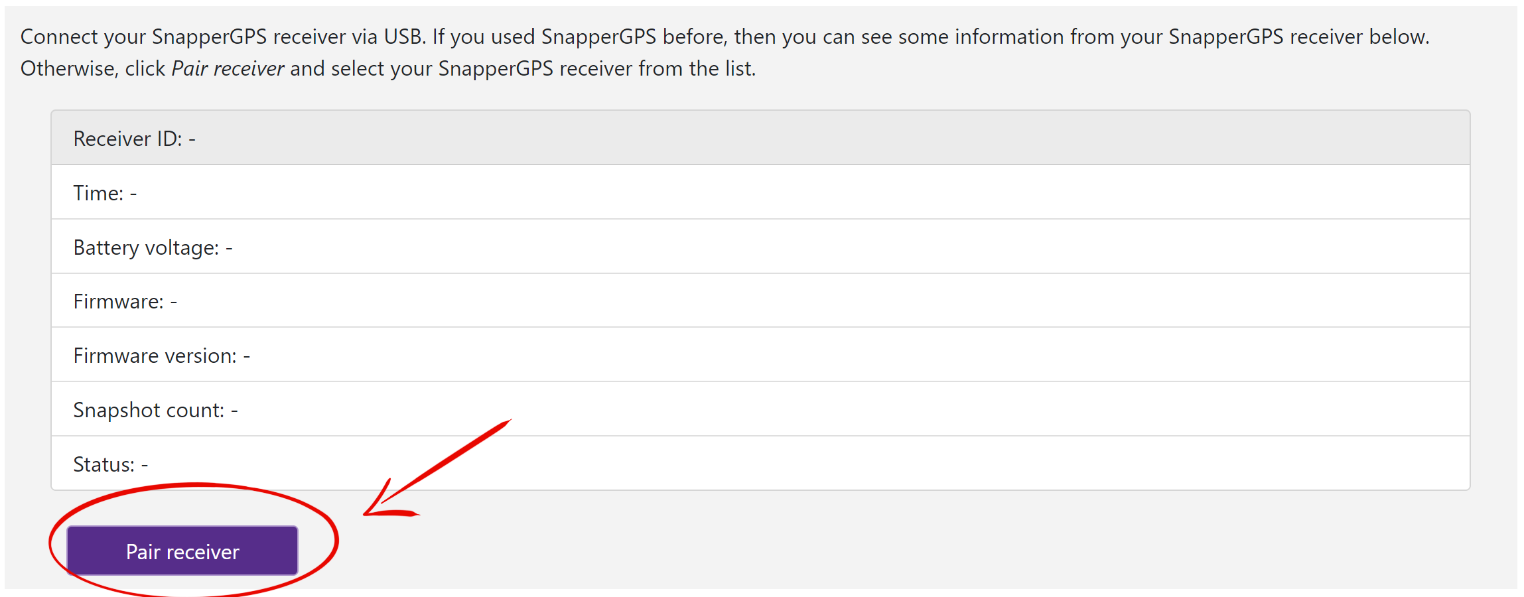
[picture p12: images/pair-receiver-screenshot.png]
Configure page before pairing a SnapperGPS receiver
|  |
|:--:|
| *Figure 6: Configure page before pairing a SnapperGPS receiver.* |

## Check the battery voltage.

If you successfully connected your SnapperGPS receiver to the web app, then you should see information about your SnapperGPS receiver on the top of the website. Check that the battery is charged, i.e., the battery voltage is around 4.1 V. If the battery is not charged, do so first before you continue.

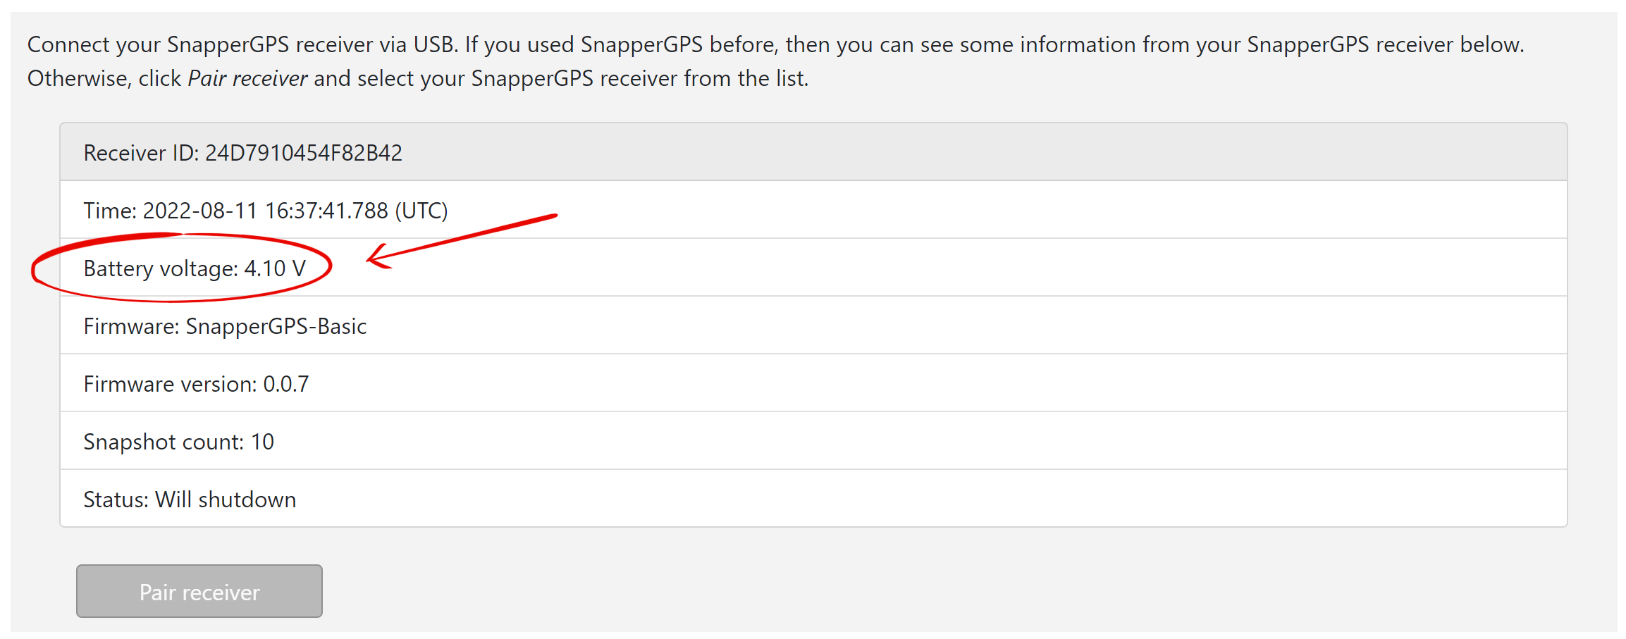
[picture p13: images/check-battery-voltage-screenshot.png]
Configure page showing battery voltage
|  |
|:--:|
| *Figure 7: Configure page showing battery voltage.* |

## Configure your SnapperGPS receiver.

Follow the steps on the same page of the web app to configure your SnapperGPS receiver for a test deployment. As start and end time, just select a short time period in the near future.

Check that the text below the “Configure” button reads “Your receiver is configured.”

Unplug your SnapperGPS receiver from USB. Immediately, the green LED should flash several times. If it does not flash or the red LED flashes, then your SnapperGPS receiver is not configured.

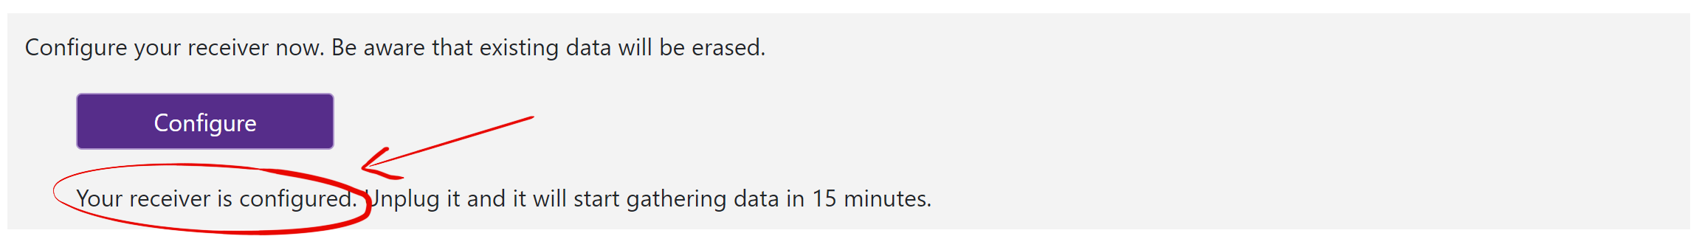
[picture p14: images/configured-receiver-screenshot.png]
Configure page after configuring a SnapperGPS receiver
|  |
|:--:|
| *Figure 8: Configure page after configuring a SnapperGPS receiver.* |

## Record some data.

Move your SnapperGPS receivers outside. Place it in a way that the antenna points upwards towards the sky. Ensure that the the board is not placed on a conductive surface and no conducting materials are directly placed on the board without isolation. (This includes antenna and battery.)

When your SnapperGPS receiver has not started to record data, then both LEDs will jointly flash in a regular interval. Once it has started to record data, the green LED will flash whenever it captures data. After all data has been recorded, the red LED will flash several times. However, you do not need to wait until this happens.

| SnapperGPS receivers recording data |
|:--:|
| *Figure 9: SnapperGPS receivers recording data.* |

## Upload your data.

Connect you SnapperGPS receiver again via USB and go to the Upload page of [https://snappergps.info/](https://snappergps.info/). Follow the instructions there to upload your raw data to our server.

Once your data has been processed, you should be able to see the final computed track on the download page.

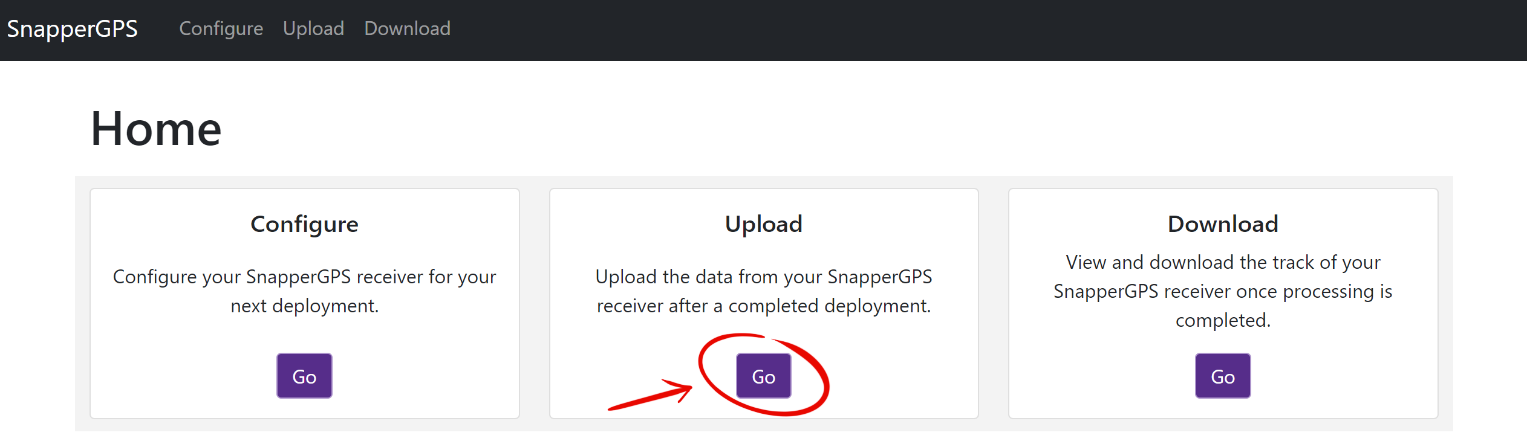
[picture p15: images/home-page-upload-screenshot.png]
Home page of https://snappergps.info/
|  |
|:--:|
| *Figure 10: Home page of https://snappergps.info/.* |

| A SnapperGPS receiver with its recorded track |
|:--:|
| *Figure 11: A SnapperGPS receiver with its recorded track.* |

## Further resources.

If you want to post-process your data, for example, smooth it to get better accuracy or plot it on an interactive map, and you have a little bit familiarity with the Python programming language, then you can find some scripts in [this repository](https://github.com/SnapperGPS/snappergps-scripts).

If you want to build a housing for your SnapperGPS receiver, then you can find some inspiration in [this repository](https://github.com/SnapperGPS/snappergps-housings). Potential housings include vacuum sealing, heat shrinking, milled plastic, or 3D printing. Make sure that the chosen method is suitable for your deployment environment.

Your SnapperGPS receiver exposes three general-purpose input-output (GPIO) pins that you can use to connect an external sensor or a trigger. Check out [the PCB design](https://github.com/SnapperGPS/snappergps-pcb) and [the firmware](https://github.com/SnapperGPS/snappergps-firmware) to learn more about this possibility.

##

This documentation is licensed under a
[Creative Commons Attribution 4.0 International License][cc-by].

[][cc-by]

[cc-by]: http://creativecommons.org/licenses/by/4.0/
[cc-by-image]: https://i.creativecommons.org/l/by/4.0/88x31.png

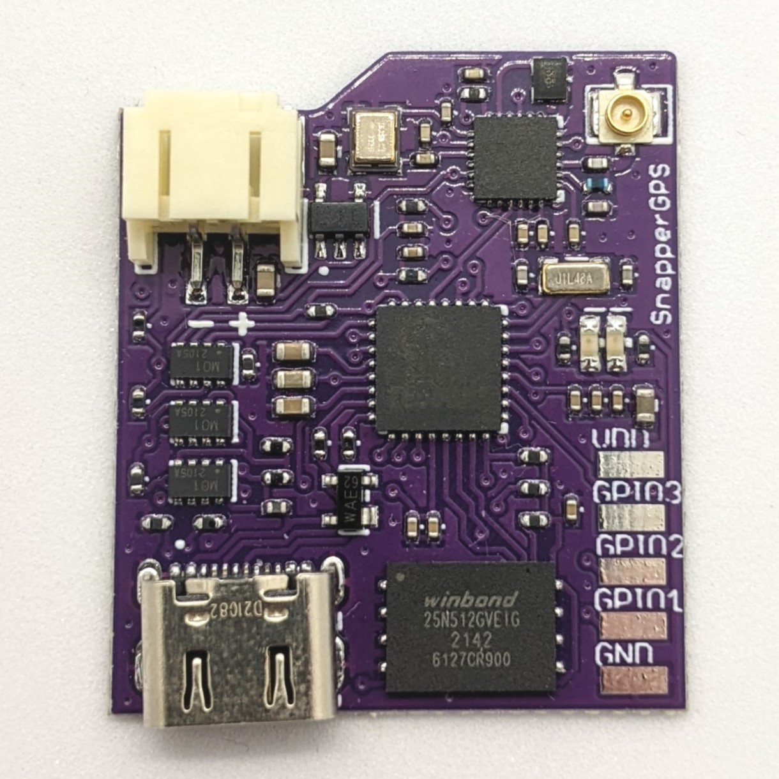
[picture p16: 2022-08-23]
images/assembled2.jpg

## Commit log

2022-06-07 Add hardware and hardware docs
    [SnapperGPS_1_0_0_BOM.csv, copper_bottom.gbr, copper_top.gbr, drills.xln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]
2022-06-08 Add note regarding antenna attachment
2022-06-08 Increment version number
    [snappergps_1_0_0.sch]
2022-06-20 Add PCB manufacturing parameters; add acknowledgement for image
    Remove white space
2022-07-04 Add workflow; add info on substitutes to BOM; restructure; tweak white space; change battery
2022-08-25 Add picture showing incorrect JST-PH connector
2022-10-14 Add note on shortening the board
2025-08-21 Update README.md with SAW filter sub

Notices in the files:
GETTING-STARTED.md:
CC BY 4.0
